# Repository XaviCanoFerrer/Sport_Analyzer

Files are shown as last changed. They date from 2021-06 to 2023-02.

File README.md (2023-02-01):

# Sport_Analyzer

Sport Analyzer is a battery powered acquisition and visualization device for measuring sport performance and rehabilitation. The device interfaces with an incremental encoder and a load cell enabling sport scientists and coaches and rehabilitators to collect and visualize the data without the need of a computer or software interaction.

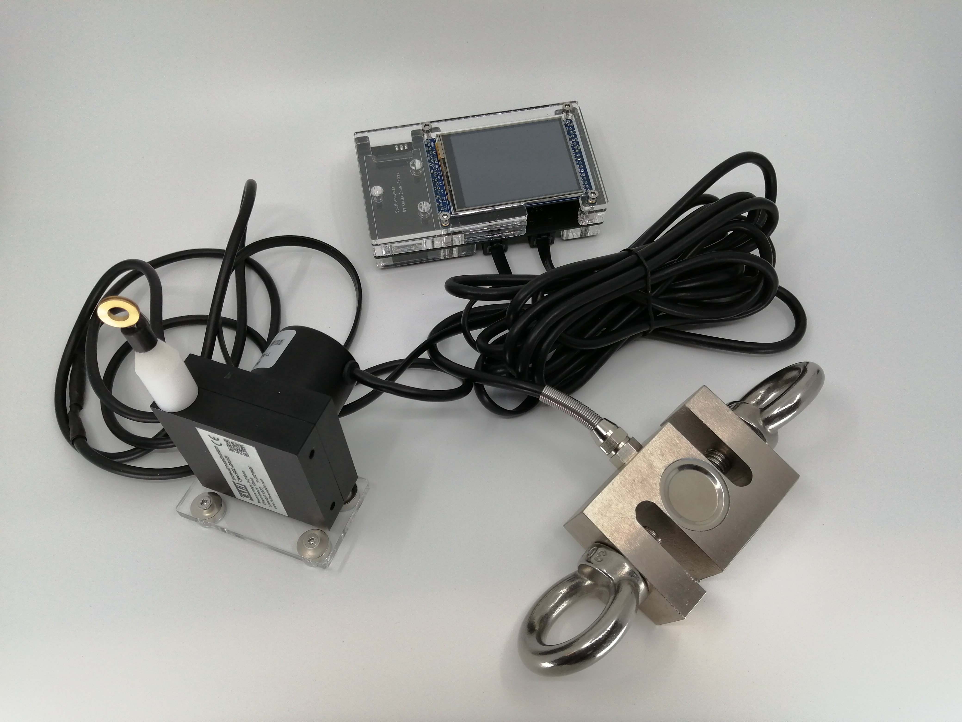
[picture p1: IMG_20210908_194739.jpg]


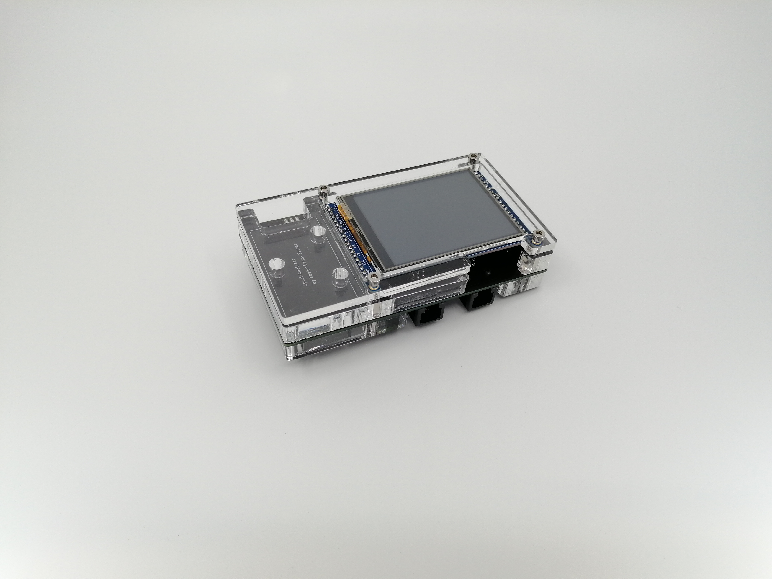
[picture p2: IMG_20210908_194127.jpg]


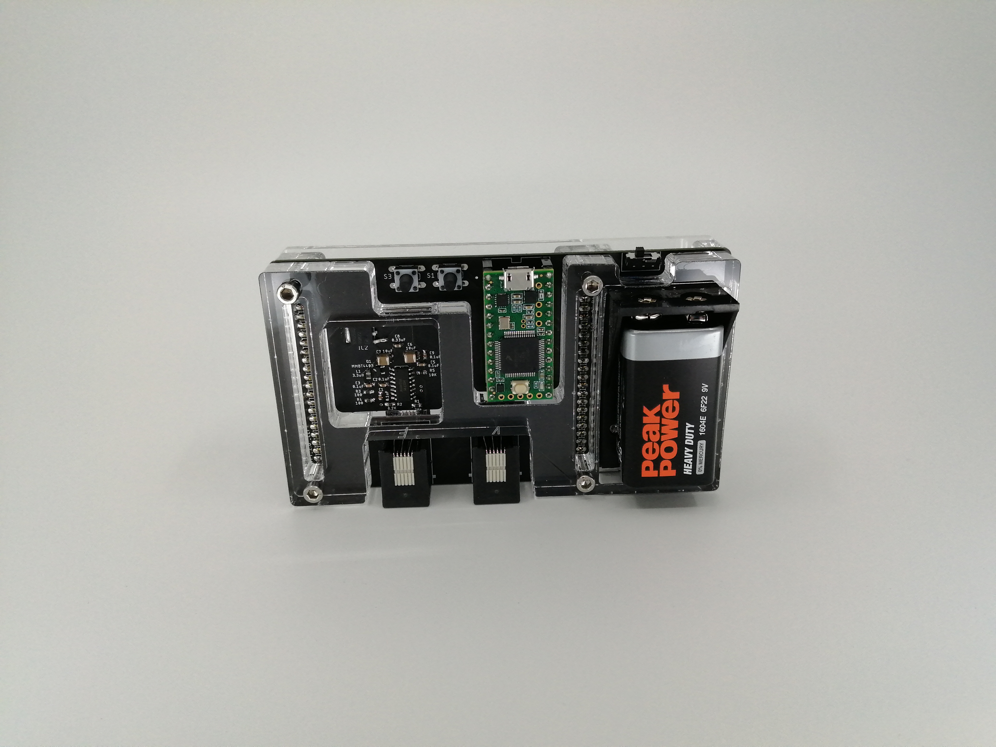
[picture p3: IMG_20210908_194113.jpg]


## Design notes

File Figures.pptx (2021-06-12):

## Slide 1

RJ12 cable – load cell connection

Cut the blue wire

E+

E-

A-

A+

Shield

Load cell wires

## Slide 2

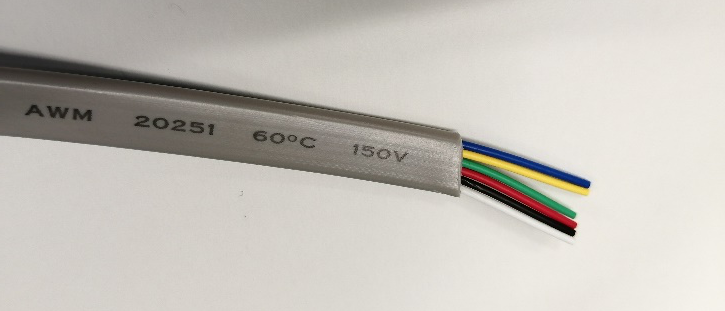
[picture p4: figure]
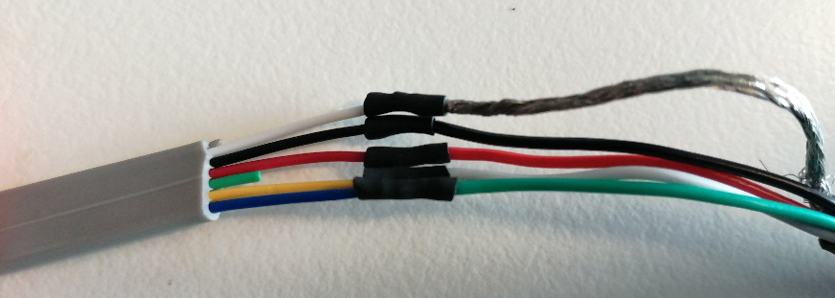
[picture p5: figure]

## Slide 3

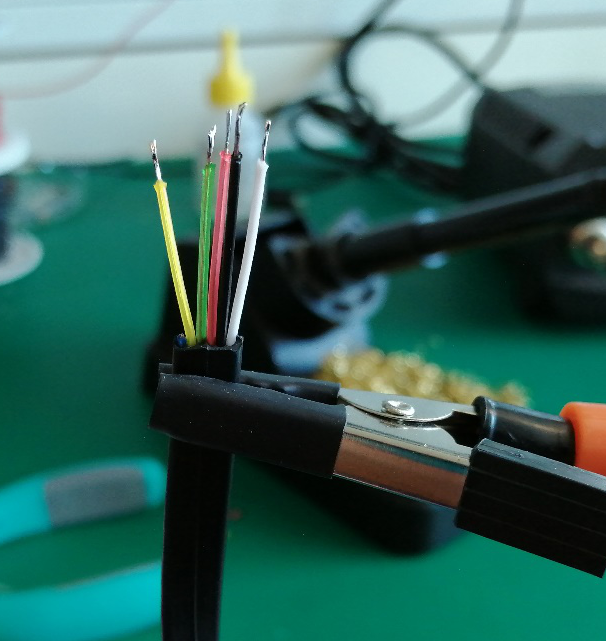
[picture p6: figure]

1

2

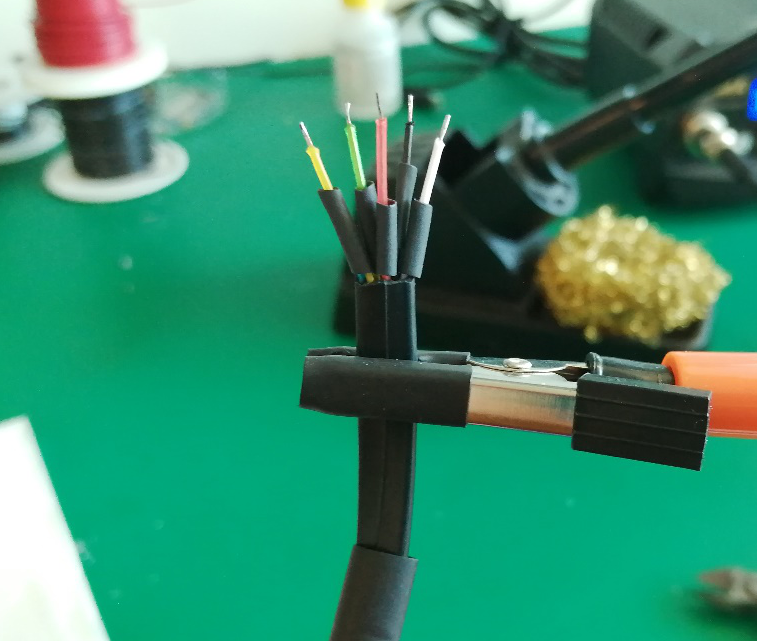
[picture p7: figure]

3

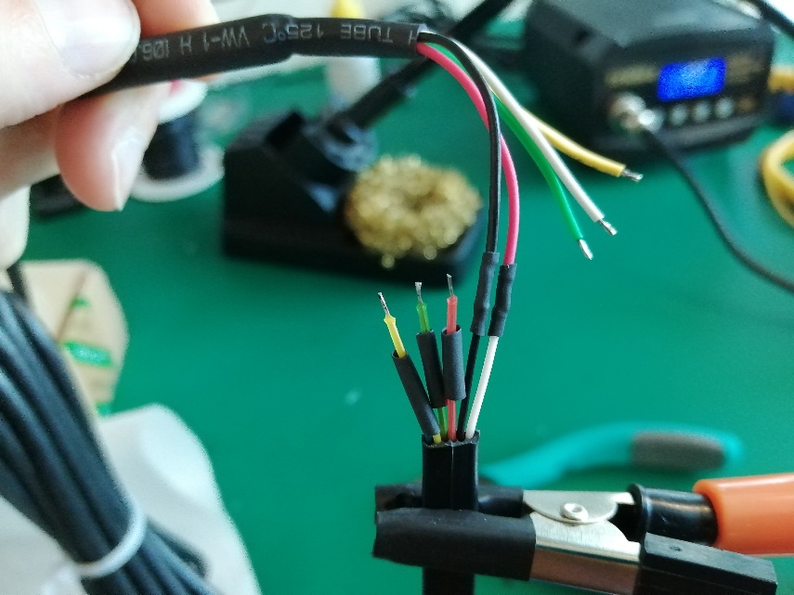
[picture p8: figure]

4

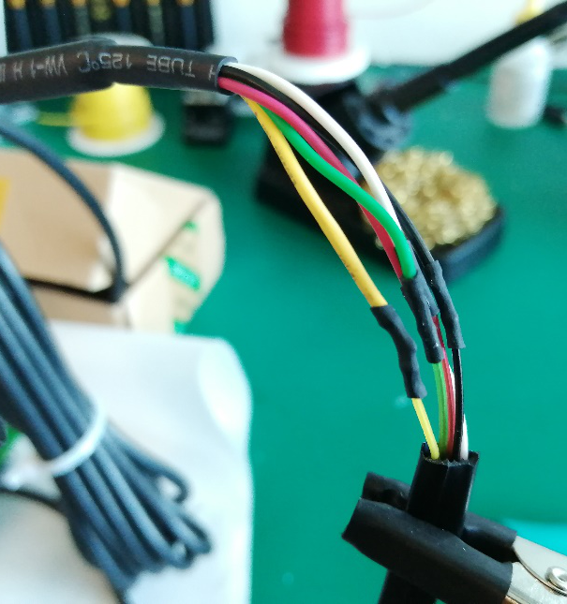
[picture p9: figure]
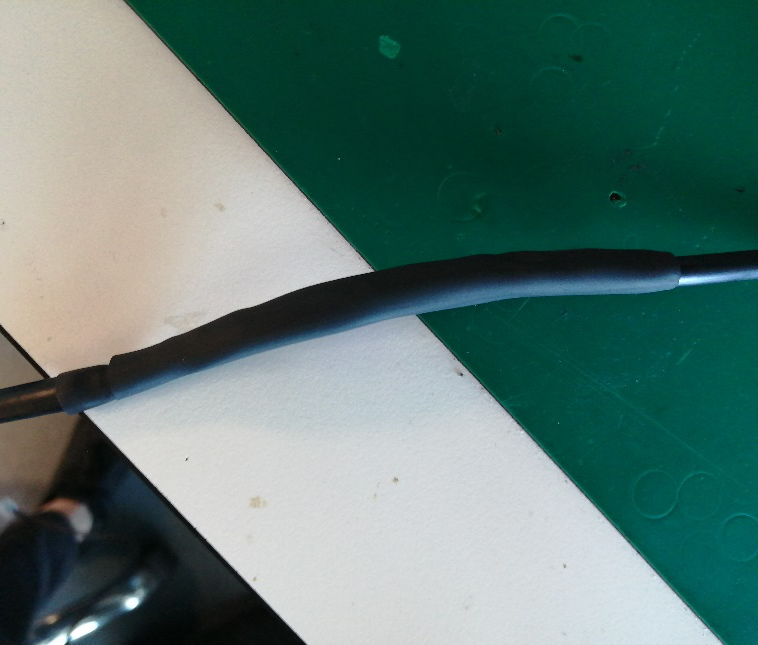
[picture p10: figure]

5

6

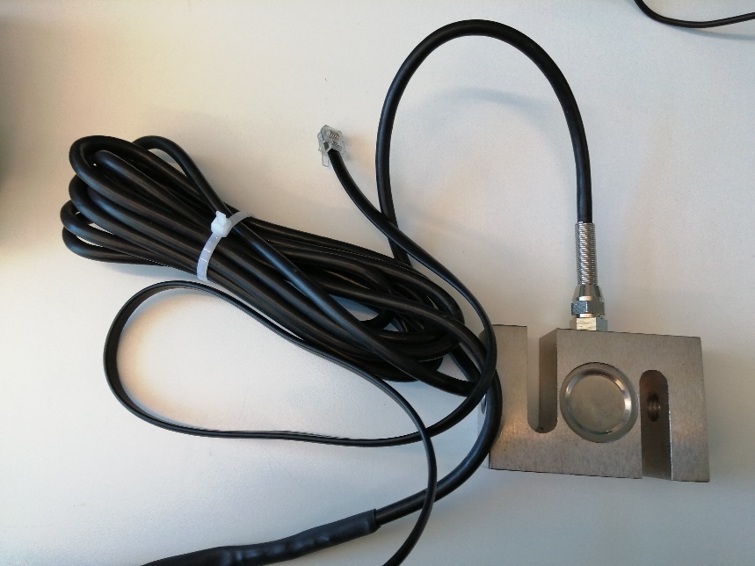
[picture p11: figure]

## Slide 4

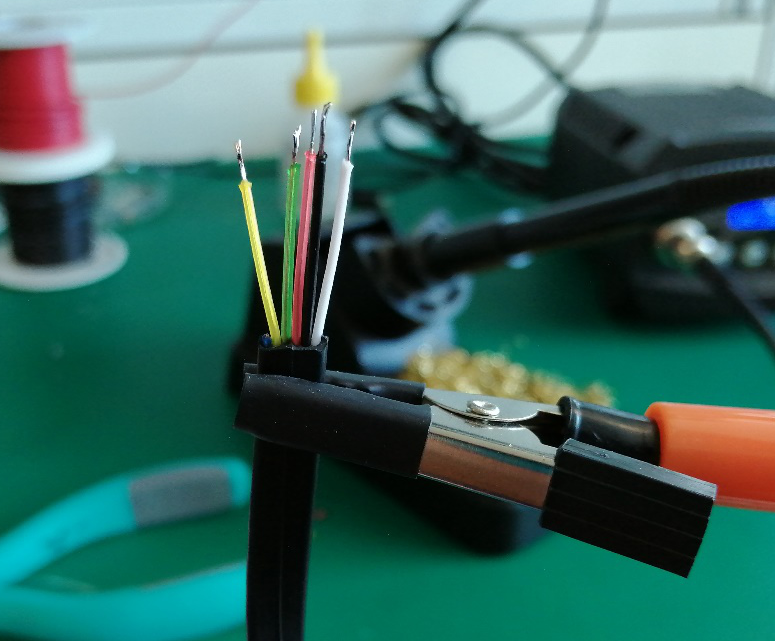
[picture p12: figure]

1

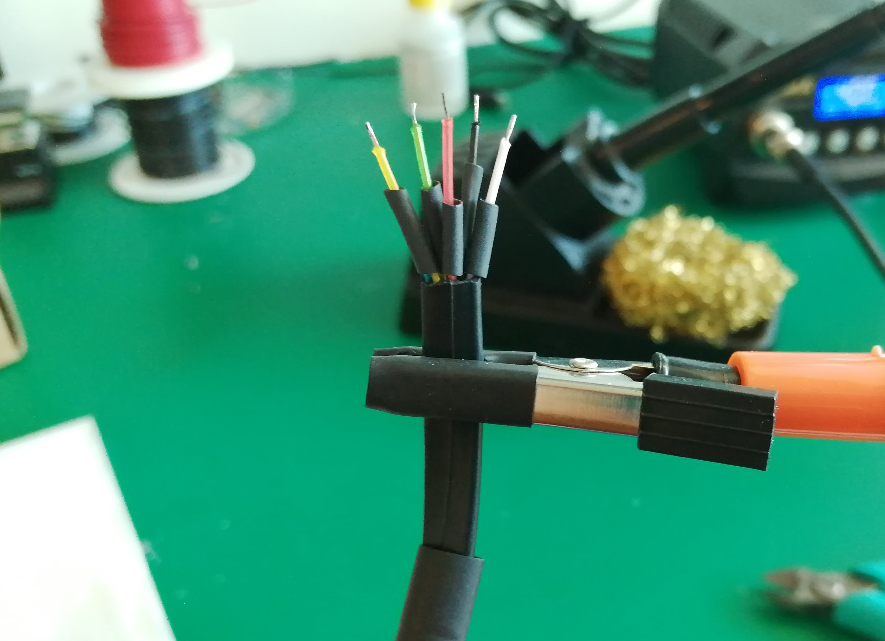
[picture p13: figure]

2

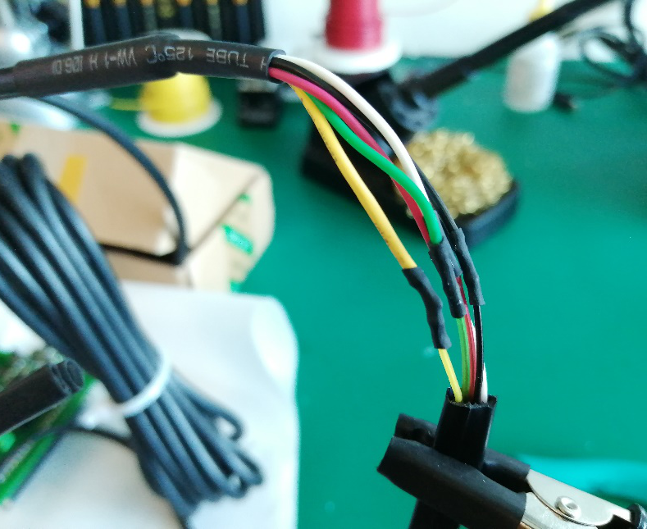
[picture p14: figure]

3

4

5

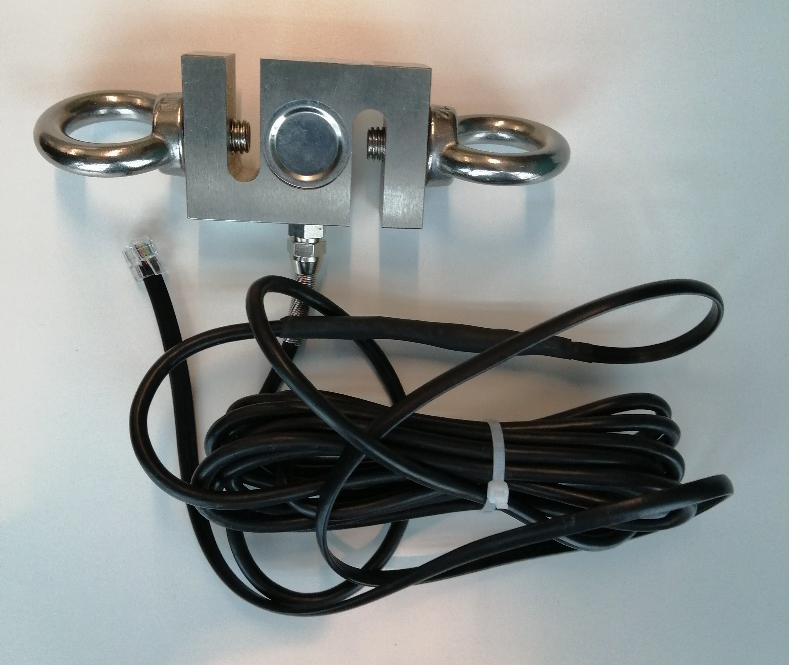
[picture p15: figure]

6

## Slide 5

RJ12 cable – optical encoder connection

Cut the green wire

Shield

GND

5V

B

A

Encoder wires

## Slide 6

RJ12 cable – load cell connection

RJ12 cable – optical encoder connection

Cut the blue wire

Cut the green wire

E+

E-

A-

A+

Shield

Shield

GND

5V

B

A

Load cell wires

Encoder wires

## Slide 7

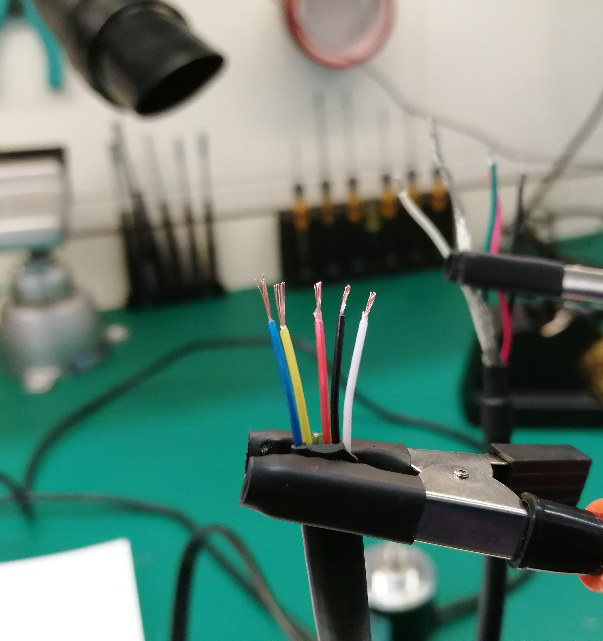
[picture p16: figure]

1

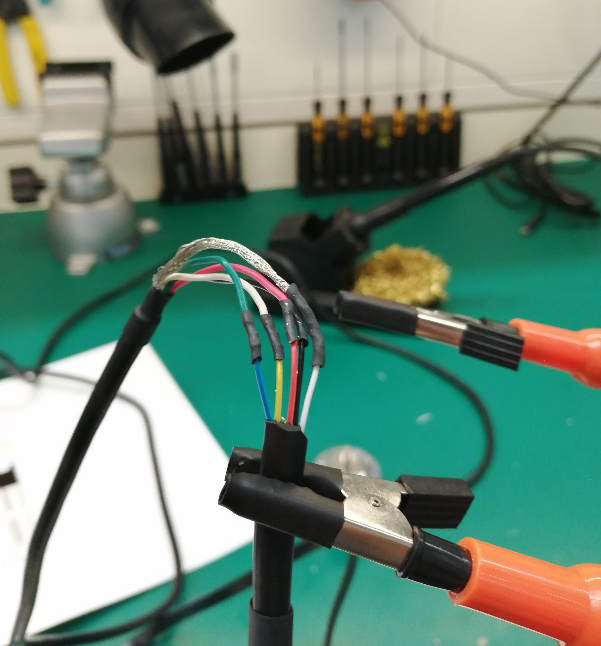
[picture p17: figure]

2

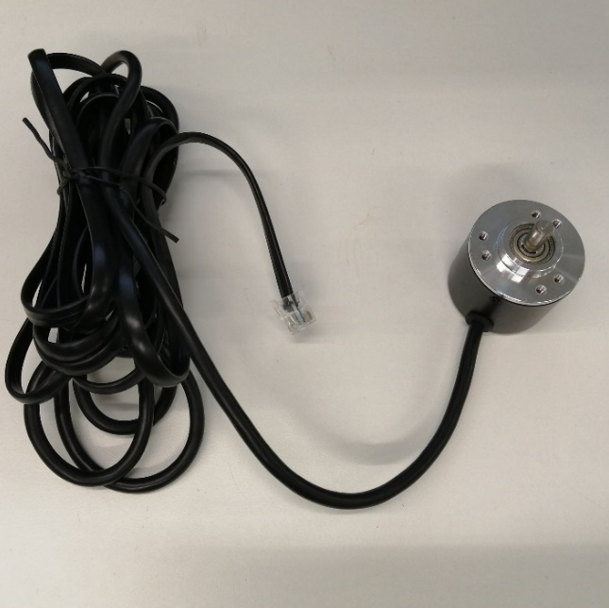
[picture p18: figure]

3

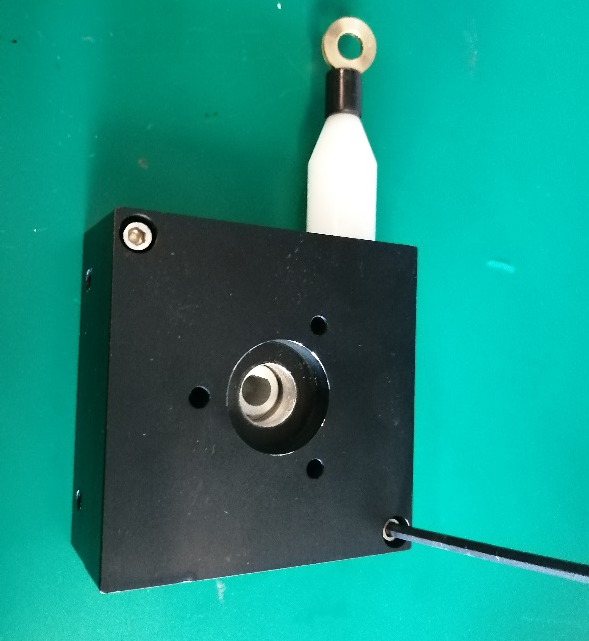
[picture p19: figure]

4

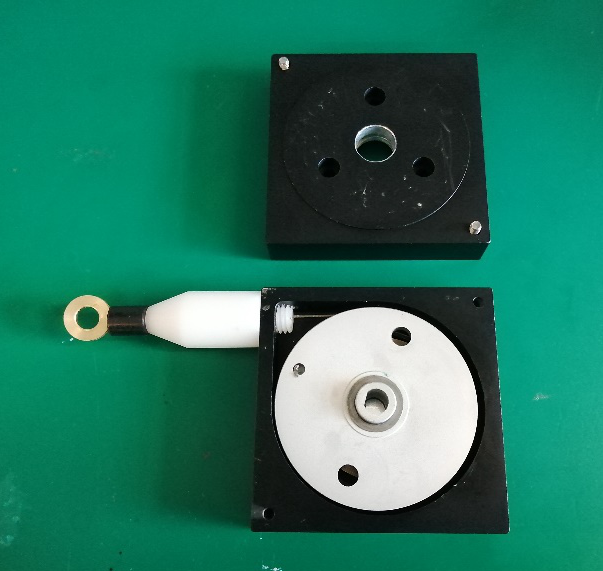
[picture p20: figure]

5

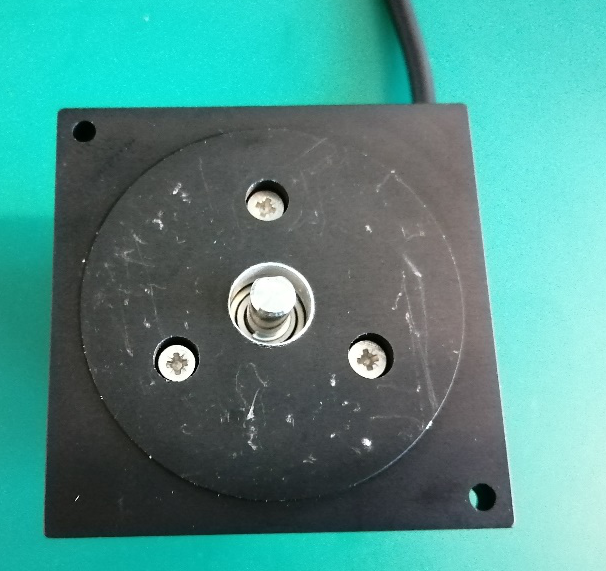
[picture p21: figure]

6

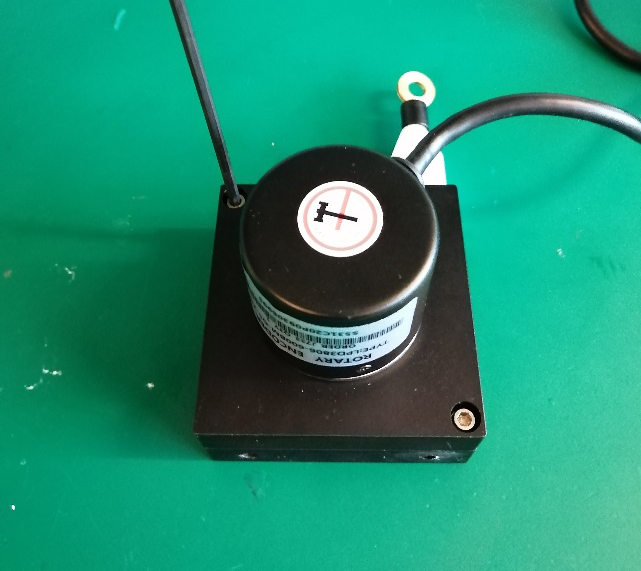
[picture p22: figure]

7

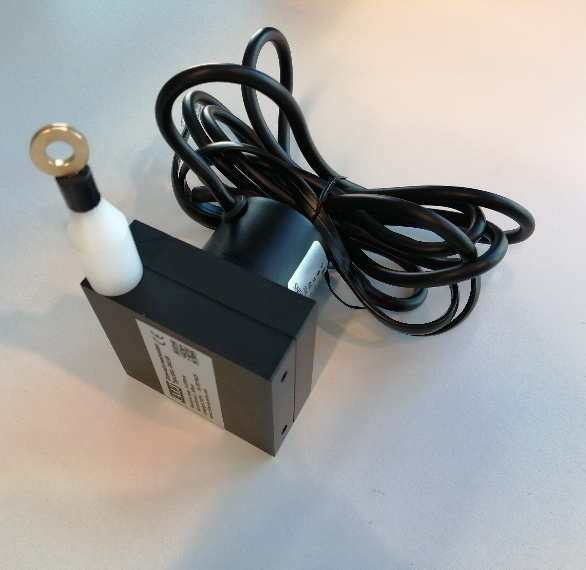
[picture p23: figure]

8

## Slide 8

RJ12 cable – resistive sensor connection

Cut the blue, yellow and white wires

5V

GND

Signal

Resistive sensor wires

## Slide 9

RJ12 cable – load cell connection

RJ12 cable – optical encoder connection

RJ12 cable – electrogoniometer connection

Cut the blue wire

Cut the green wire

Cut the blue, yellow and white wires

Load cell wires

E+

E-

A-

A+

Shield

Encoder wires

Shield

GND

5V

B

A

Electrogoniometer
sensor wires

GND

5V

Signal

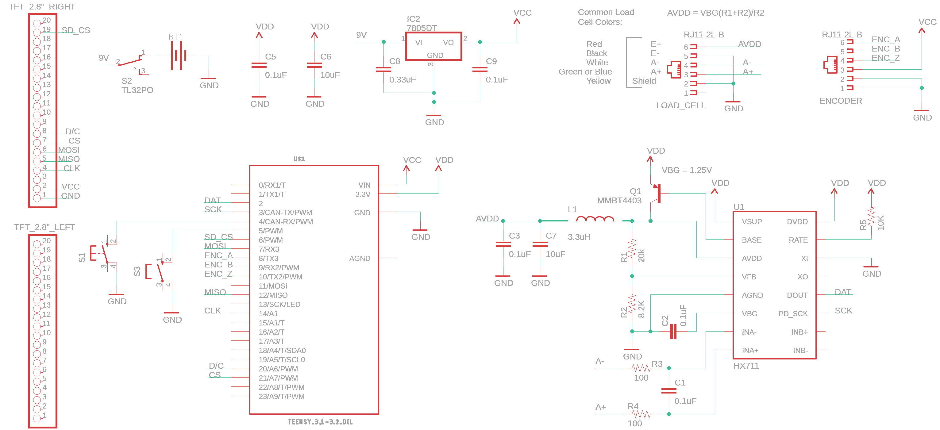
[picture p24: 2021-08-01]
Schematic.png

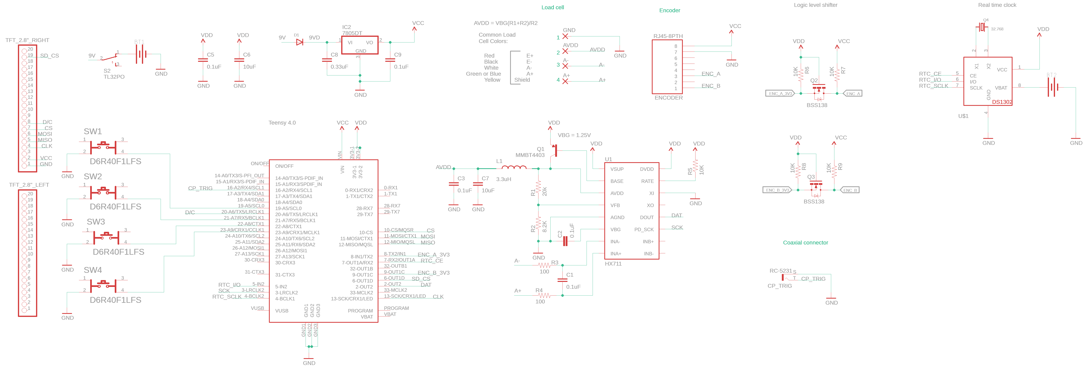
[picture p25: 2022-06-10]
Chronojump version/Teensy 4.0 version/Design files/Sport Analyzer Chronojump Teensy 4 schematic.png

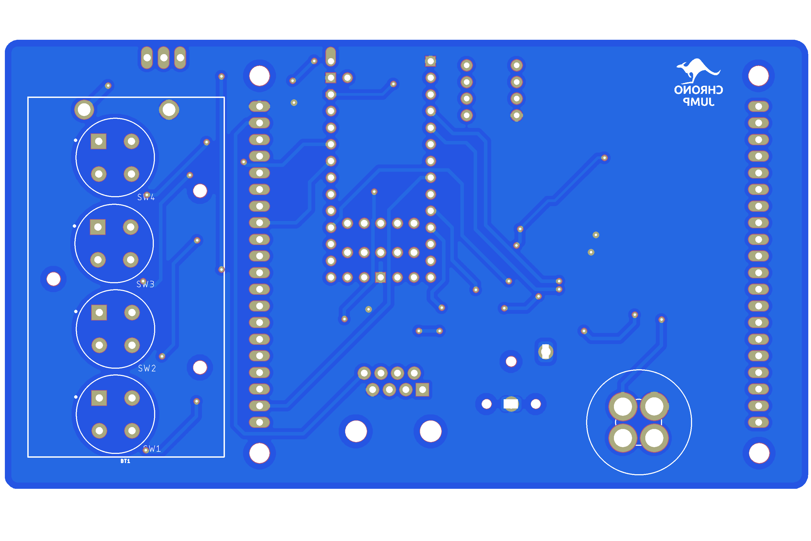
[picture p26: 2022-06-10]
Chronojump version/Teensy 4.0 version/Design files/Sport Analyzer Chronojump Teensy 4 (4 buttons)bottom.png

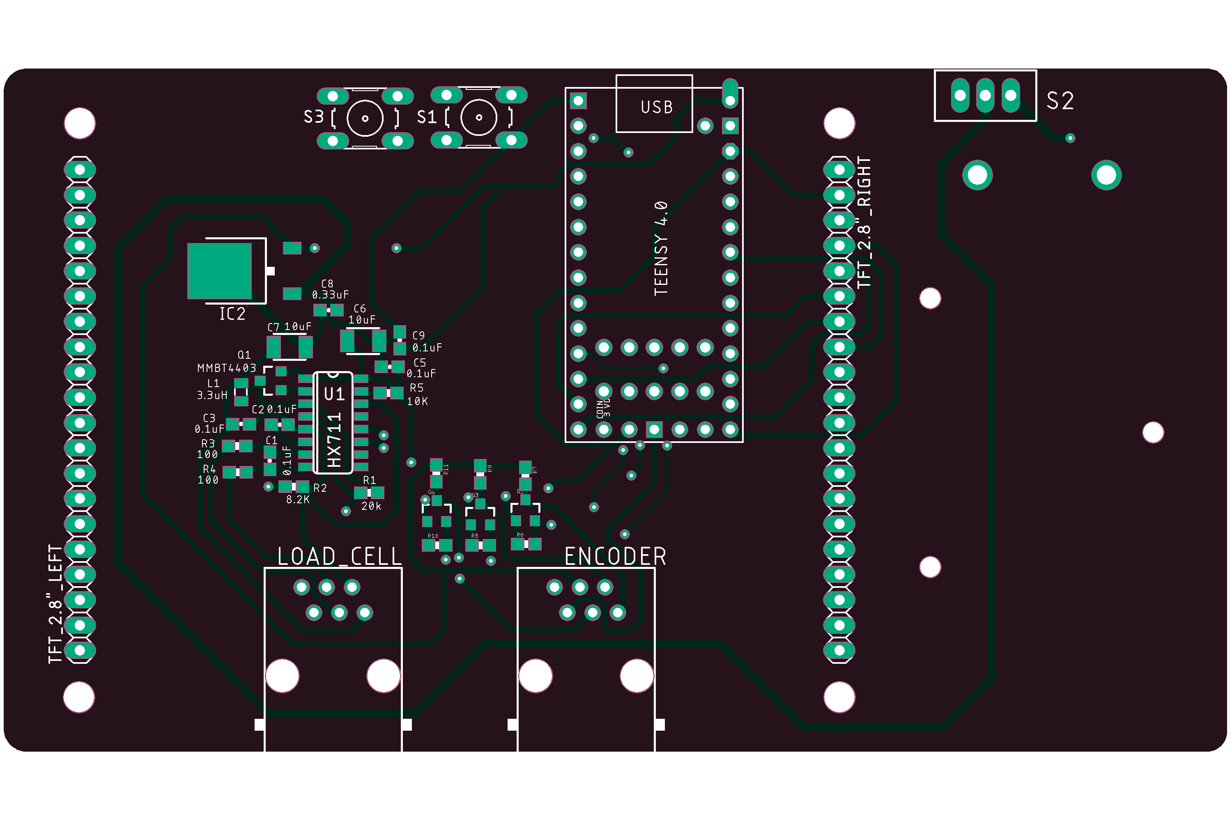
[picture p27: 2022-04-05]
Teensy 4 version/Design files/Electronics/Sport Analyzer Teensy4.png

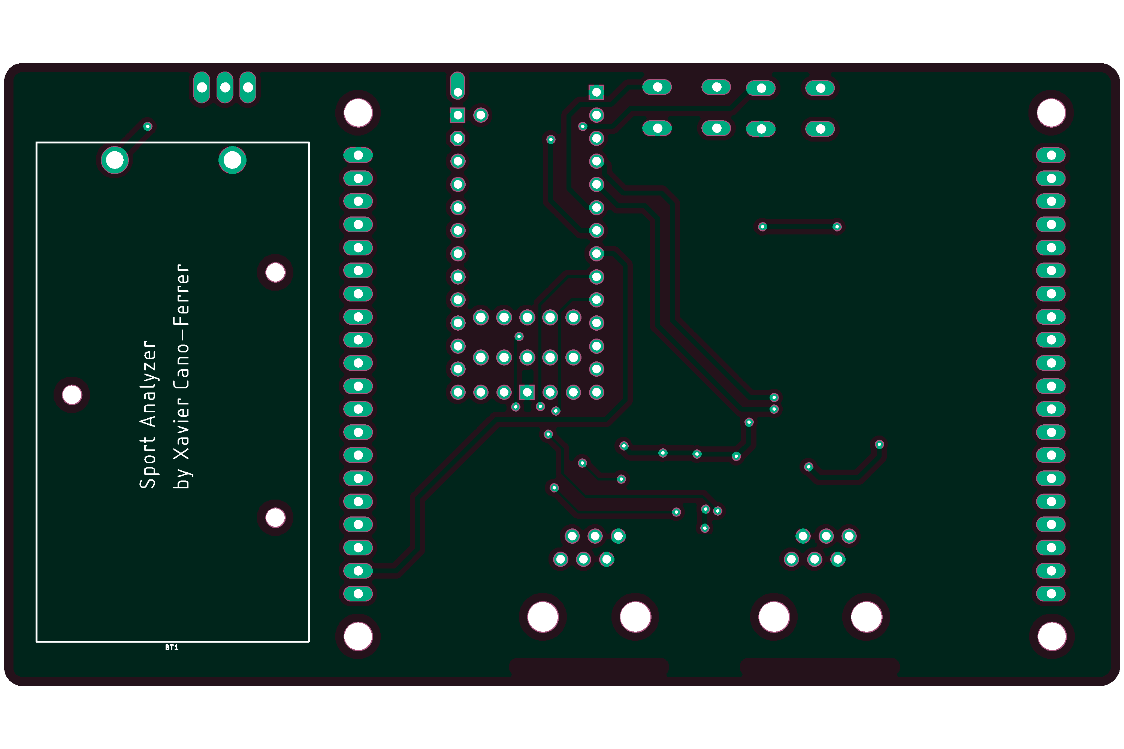
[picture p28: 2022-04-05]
Teensy 4 version/Design files/Electronics/Sport Analyzer Teensy4 bottom.png

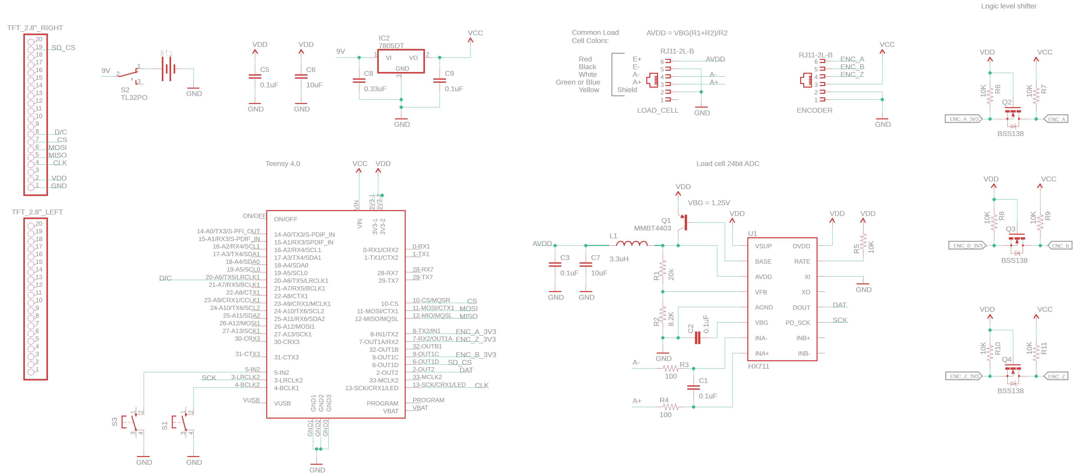
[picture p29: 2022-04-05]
Teensy 4 version/Design files/Electronics/Sport Analyzer Teensy4 schematic.png

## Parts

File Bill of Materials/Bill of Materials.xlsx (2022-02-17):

Component | Supplier | Reference | Cost per unit(£) | Quantity | Total cost
PCB | JLC PCB | - | 0.355 | 1 | 0.355
Case top | - | https://github.com/XaviCanoFerrer/Sport_Analyzer/tree/main/Manufacturing%20files |  | 1
Case middle 1 | - |  |  | 1
Case middle 2 | - |  |  | 1
Case bottom | - |  |  | 1
Encoder Base | - |  |  | 1
2.8" TFT LCD with Touchscreen Breakout Board | RS Components | 124-5469 | 27.41 | 1 | 27.41
Teensy 3.2 | CPC-Farnell | SC13983 | 16.67 | 1 | 16.67
Slide Switch | Rapid Electronics | 78-3760 | 0.374 | 1 | 0.374
RJ12 Connector | RS Components | 809-4902 | 1.36 | 2 | 2.72
Pushbutton Omron B3F-1020 | RS Components | 682-1131 | 0.586 | 2 | 1.172
Ceramic capacitor 0603 0.1uF | RS Components | 264-4646 | 0.017 | 5 | 0.085
Ceramic capacitor 0603 0.33uF | RS Components | 839-2900 | 0.142 | 1 | 0.142
Resistor 0603 100 Ω 1% | RS Components | 901-3525 | 0.05 | 2 | 0.1
Resistor 0603 10 kΩ 1% | RS Components | 901-3601 | 0.046 | 1 | 0.046
Ceramic capacitor 1210 10uF | RS Components | 766-1217 | 0.55 | 2 | 1.1
Resistor 0603 20 kΩ 1% | RS Components | 901-3610 | 0.05 | 1 | 0.05
Inductor 0805 3.3 uH | RS Components | 724-2790 | 0.164 | 1 | 0.164
Resistor 0603 8.2 kΩ 1% | RS Components | 901-3591 | 0.052 | 1 | 0.052
Transistor BJT MMBT4403 | RS Components | 739-0509 | 0.067 | 1 | 0.067
Voltage regulator 7805 | RS Components | 808-4116 | 0.5 | 1 | 0.5
HX711 Load cell ADC | JLCPCB | C43656 | 0.3522 | 1 | 0.3522
RJ12 cable | Farnell | 2070346 | 1.92 | 2 | 3.84
Female pin headers | Amazon | https://www.amazon.co.uk/Aussel-Pieces-Breakaway-Connector-Arduino-PIN-2-20PCS/dp/B01M69EA9O | 0.3495 | 3 | 1.0485
Incremental encoder | Amazon | https://www.amazon.co.uk/Wisamic-Incremental-Encoder-Dc5-24v-Voltage/dp/B015GYY7XU | 16.99 | 1 | 16.99
CALT BSL-GA55 Draw-Wire Mechanism | CALT | https://www.china-encoder.com/product/economic-version-bsl-ga55-encoder-draw-wire-mechanism/ | 32.5 | 1 | 32.5
 | CALT | https://www.aliexpress.com/item/1005002782719866.html
Loac cell | Amazon | https://www.amazon.co.uk/gp/product/B07X8PZ2HX/ref=ppx_yo_dt_b_asin_title_o02_s00?ie=UTF8&psc=1 | 29.09 | 1 | 29.09
M12 Eye bolt | Amazon | https://www.amazon.co.uk/sourcing-map-Lifting-Hanging-Stainless/dp/B08NJ32ZYY | 5.545 | 2 | 11.09
Micro SD Card 32 GB | RS Components | 123-1040 | 7.294 | 1 | 7.294
Male USB A to Male USB Micro B USB Cable, 0.5m, USB 2.0 | RS Components | 182-8551 | 3 | 1 | 3
Magnet | RS Components | 136-5467 | 7.33 | 2 | 14.66
M3 hexagonal spacers and screws | Amazon | https://www.amazon.co.uk/ANTHYTA-Standoff-Assorted-Assortment-Threaded/dp/B091KJNZLB?qsid=257-8279358-2489441 | 8.99 | 1 | 8.99
9V Battery holder | Rapid Electronics | 18-2990 | 0.48 | 1 | 0.48
 |  |  |  | Total | 179.9867

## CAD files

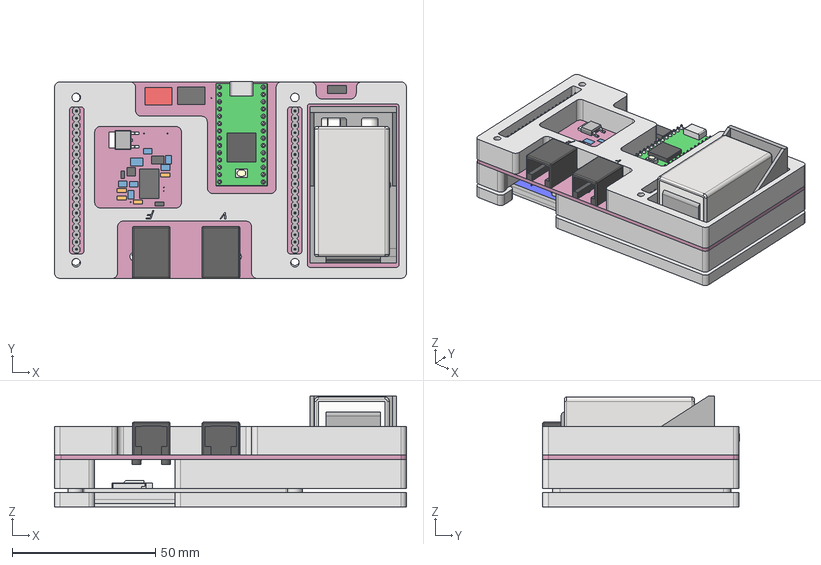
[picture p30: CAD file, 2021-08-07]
Design Files/Mechanical/Assembly.stp
122.7 x 68.7 x 38.7 mm
Bottom PMMA
Middle PMMA
Top PMMA
Adafruit 2.8TFT
RJ12 Connector x 2
9V Battery
Body_Housing
Teensy3.2
Sport Analyzer 1.0.1 PCB (2)

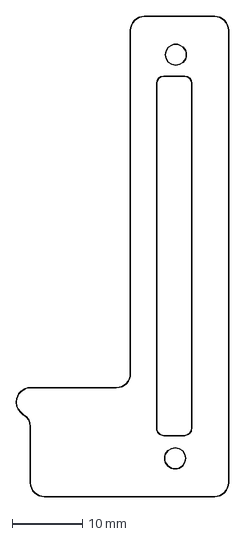
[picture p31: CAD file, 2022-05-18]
Chronojump version/Teensy 3.2 version/Manufacturing files/Case/Bottom case Chronojump 2.dxf
30.3 x 68.6 mm

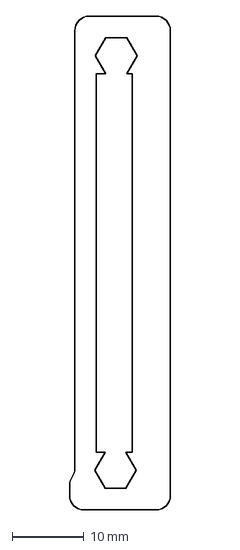
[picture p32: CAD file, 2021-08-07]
Manufacturing files/DXF files/Case Middle 2.dxf
14.0 x 68.6 mm

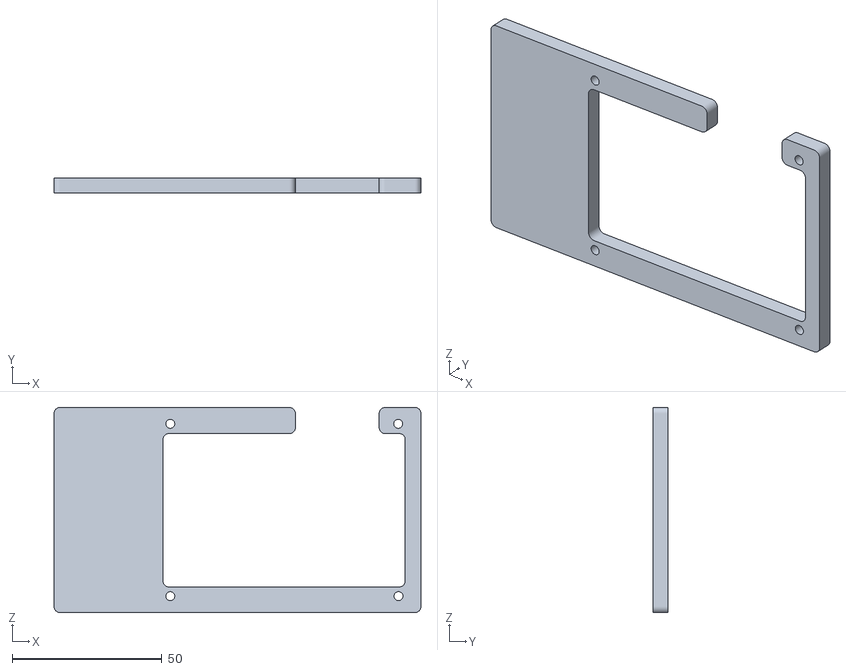
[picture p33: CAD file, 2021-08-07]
Manufacturing files/STL files/Case Top.stl
122.7 x 5.00 x 68.6

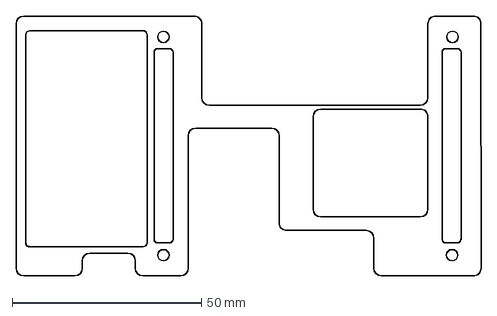
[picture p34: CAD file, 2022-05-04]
Chronojump version/Teensy 3.2 version/Manufacturing files/Case/Bottom case Chronojump 1.dxf
122.7 x 68.6 mm

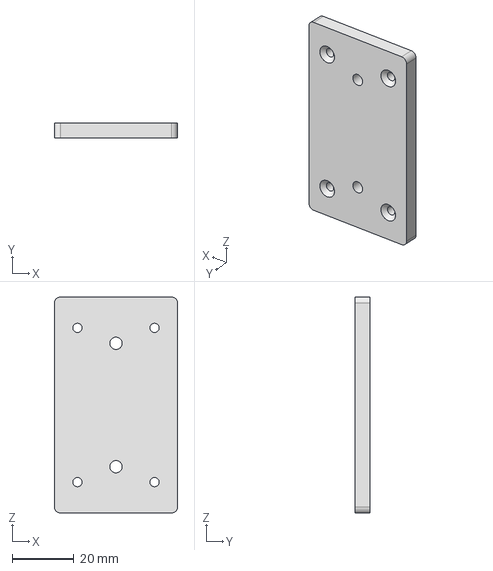
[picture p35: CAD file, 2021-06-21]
Design Files/Mechanical/Encoder base.stp
40.0 x 5.00 x 70.0 mm

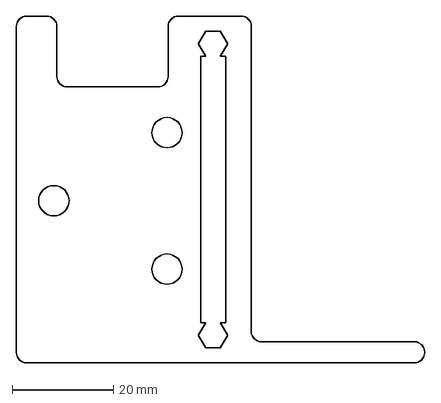
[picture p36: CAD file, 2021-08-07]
Manufacturing files/DXF files/Case Middle 1.dxf
80.7 x 68.6 mm

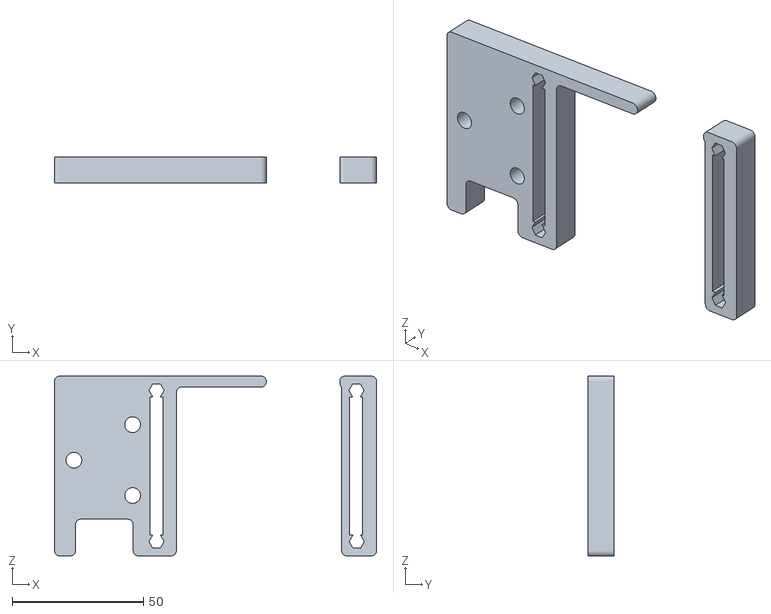
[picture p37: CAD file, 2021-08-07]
Manufacturing files/STL files/Case Middle.stl
122.7 x 10.0 x 68.6

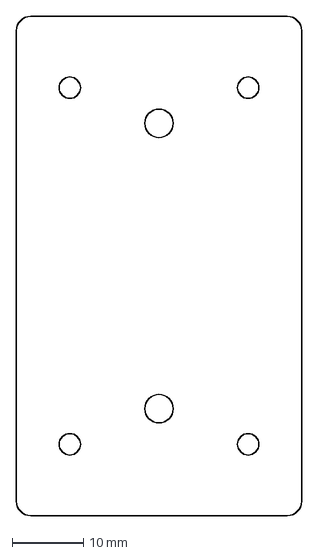
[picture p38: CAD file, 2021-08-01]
Manufacturing files/DXF files/Encoder base.dxf
40.0 x 70.0 mm

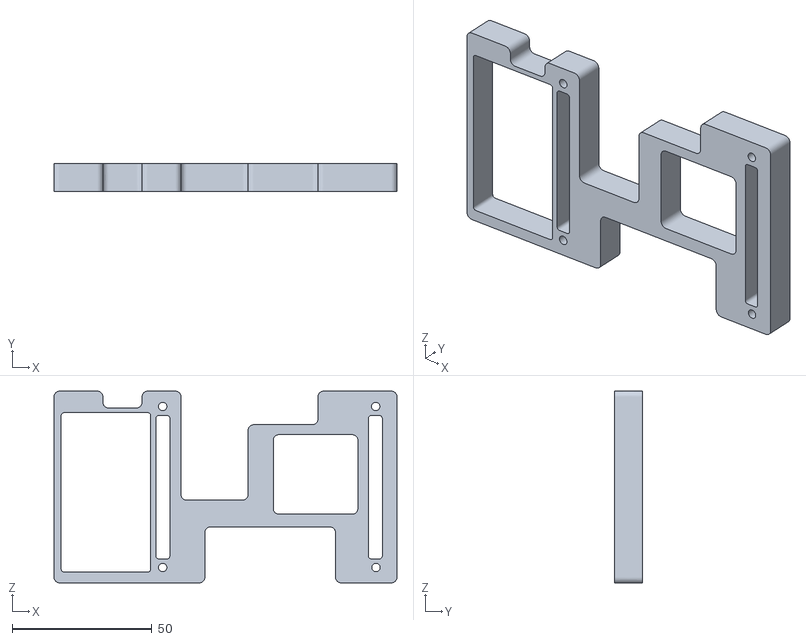
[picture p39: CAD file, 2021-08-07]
Manufacturing files/STL files/Case Bottom.stl
122.7 x 10.0 x 68.6

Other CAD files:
Chronojump version/Teensy 3.2 version/Design files/Case/Bottom PMMA Chronojump.ipt
Chronojump version/Teensy 3.2 version/Design files/Case/OldVersions/Bottom PMMA Chronojump.0021.ipt
Chronojump version/Teensy 3.2 version/Design files/Case/OldVersions/Bottom PMMA Teensy4.0018.ipt
Design Files/Mechanical/0603-CAP.ipt
Design Files/Mechanical/0603-RES.ipt
Design Files/Mechanical/0805.ipt
Design Files/Mechanical/1210.ipt
Design Files/Mechanical/1X20.ipt
Design Files/Mechanical/9V Battery.ipt
Design Files/Mechanical/Adafruit 2.8TFT.ipt
Design Files/Mechanical/Assembly3.iam
Design Files/Mechanical/B3F-10XX.ipt
Design Files/Mechanical/BATTCON_9V.ipt
Design Files/Mechanical/Board.ipt
Design Files/Mechanical/Body_Housing 9V Battery.ipt
Design Files/Mechanical/Bottom PMMA.ipt
Design Files/Mechanical/Encoder base.ipt
Design Files/Mechanical/Middle PMMA.ipt
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

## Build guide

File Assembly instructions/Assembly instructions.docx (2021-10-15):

Assembly and calibration instructions

1- Acquire the components

Order the printed circuit board and order the components described on the bill of materials: https://github.com/XaviCanoFerrer/Sport_Analyzer/tree/main/Bill%20of%20Materials. The PCB can be ordered on JLCPCB: https://jlcpcb.com/.

2- Manufacture the Sport Analyzer case

The case has been designed in a way that the components can be laser cut or 3D printed, which are the two most common manufacturing processes available for makers (Figure 1). The files can be found on https://github.com/XaviCanoFerrer/Sport_Analyzer/tree/main/Manufacturing%20files.

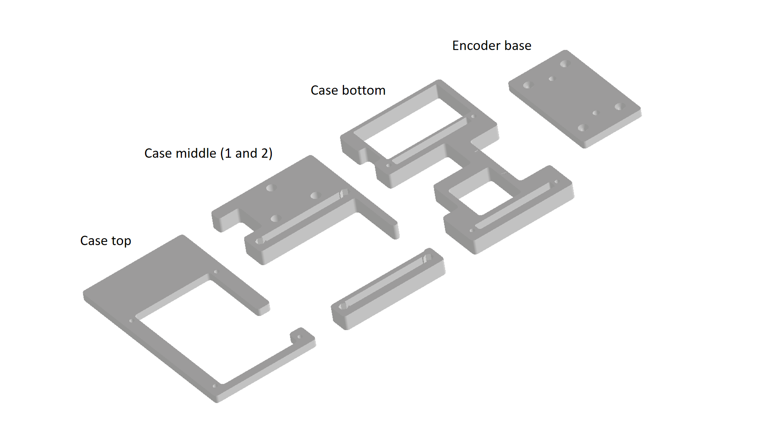
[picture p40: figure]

Figure 1: Components of the case.

3- Solder the components on the Board

In order to hold the surface mount components (SMD) it is highly recommended to use tweezers to hold the small capacitors and resistors. All components can be soldered by adding solder on one of the pads and then fuse the solder by touching it with the soldering iron while holding the component in place helping yourself with the tweezers (Figure 2).

Figure 2: Components to be soldered.

4- Case assembly

The three components of the case (top, middle and bottom) are assembled using four hexagonal spacers and eight M3 screws that hold them together (Figure 3).

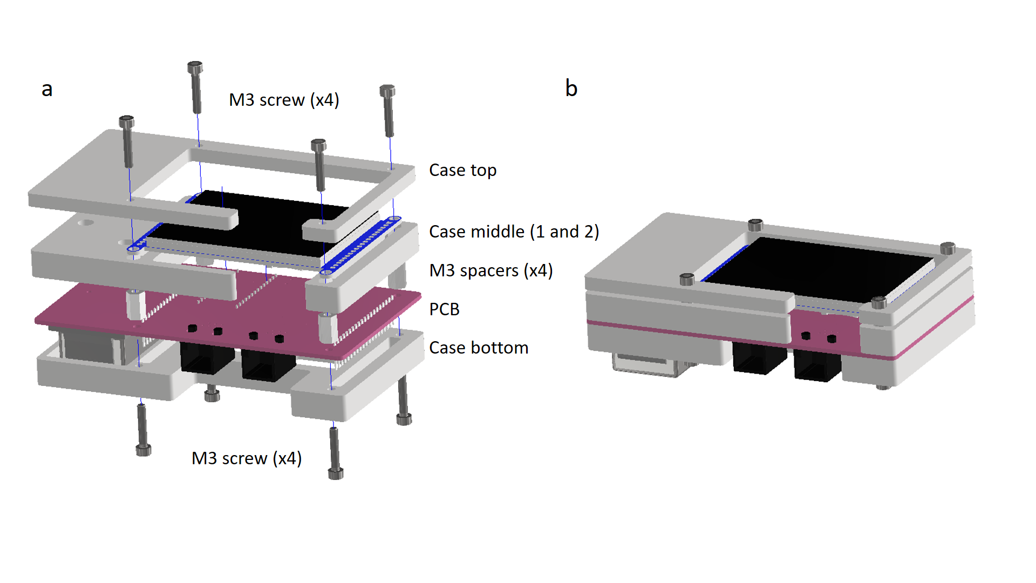
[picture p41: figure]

Figure 3: Exploded and assembled views of the case with the board.

5- RJ12 cable connections

The load cell and the encoder are connected with the Sport Analyzer using RJ12 (6 wire) connections. In Figure 4 is described which wires must be soldered with which ones to have a successful connection with the sensor leads.

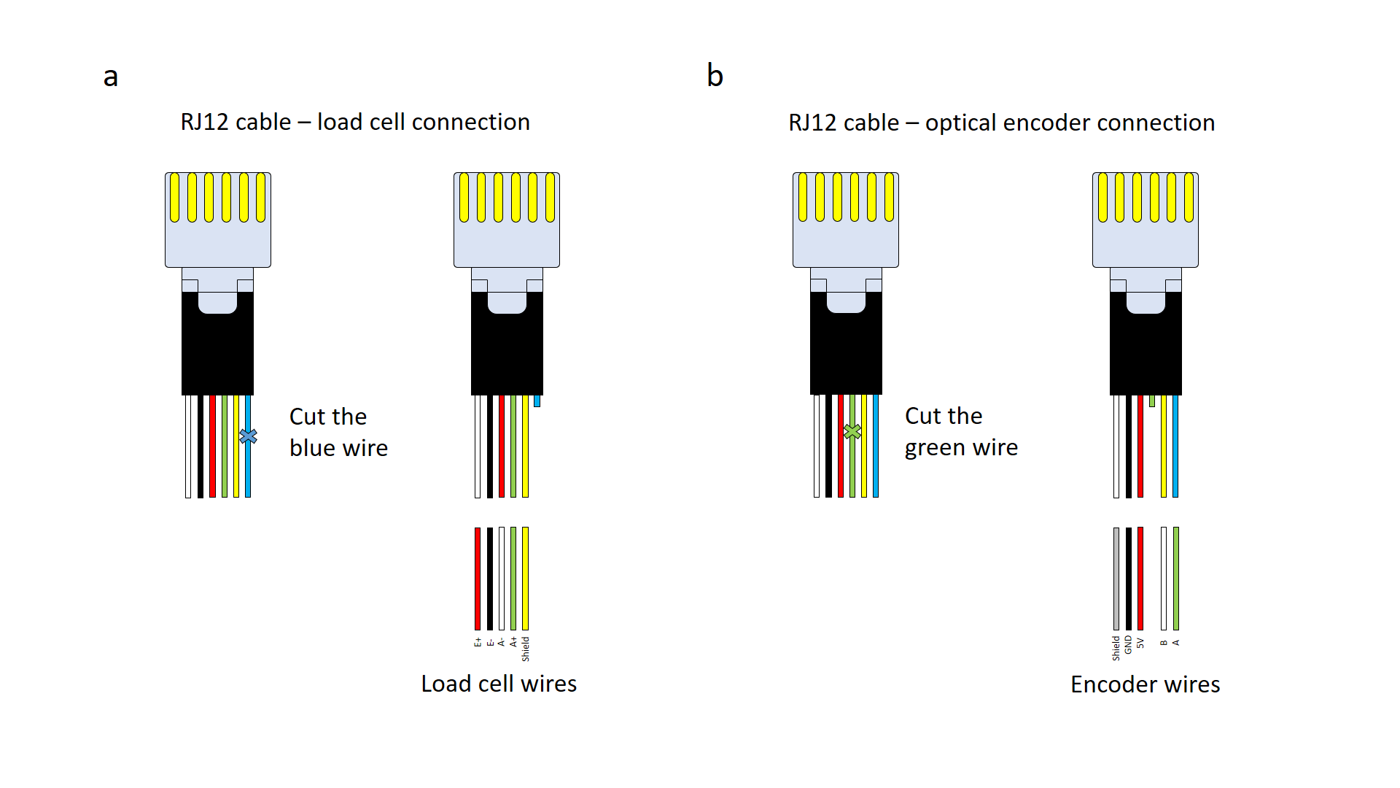
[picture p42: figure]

Figure 4: RJ12 cable connections for the load cell and the encoder.

6- Load cell building

The only manufacturing process on the load cell side is the soldering of the RJ12 cable with the load cell cable as described on (Figure 4a). The RJ12 cable must be strip leaving approximately 30 cm of cable from the connector to the cut. Then solder can be applied on each of the wires of both sides (Figure 5a). A big heat shrink with bigger diameter than the cable and six smaller ones can be applied on the wires (Figure 5b). Then solder each of the wires one by one and apply heat on the small heat shrinks (Figure 5c). Now surround the five small wires with the big heat shrink and apply heat getting a continuous cable again (Figure 5d-e). The final step is to screw the M12 eye bolts on both sides of the load cell (Figure 5f).

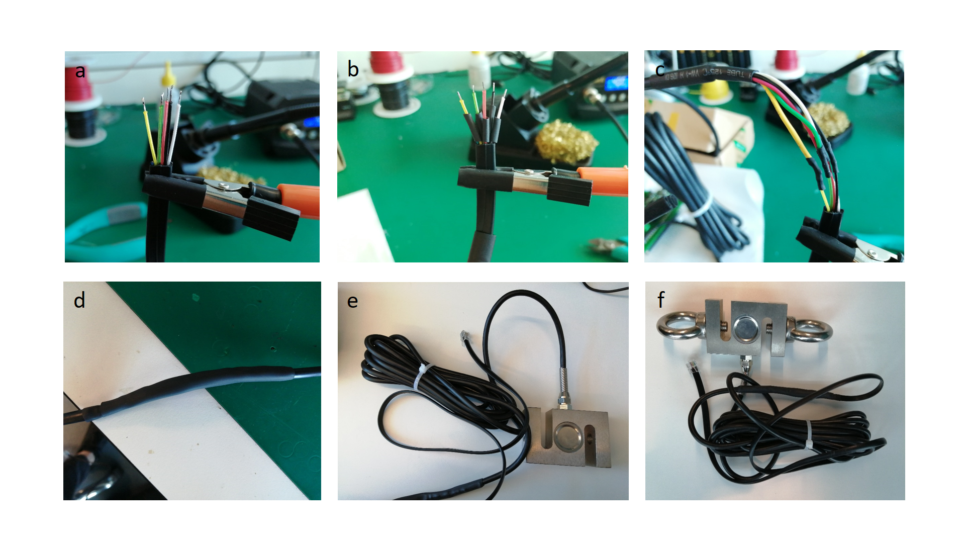
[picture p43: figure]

Figure 5. Load cell soldering and assembly process.

7- Encoder building

The encoder soldering process is very similar to the one described with the load cell. How to connect the sensor cables with the RJ12 connector can be found in Figure 4b. The RJ12 cable must be strip leaving approximately 30 cm of cable from the connector to the cut. Then solder can be applied on each of the wires of both sides (Figure 6a). A big heat shrink with bigger diameter than the cable and six smaller ones can be applied on the wires. Then solder each of the wires one by one and apply heat on the small heat shrinks (Figure 6b). Now surround the five small wires with the big heat shrink and apply heat getting a continuous cable again (Figure 6c). The next steps describe how to assemble the incremental encoder with the draw-wire mechanism which converts the rotational movement into translational movement. Place the draw-wire mechanism facing the Allen key screws up. Both M3 screws have to be removed (Figure 6d). Then the top part has to be carefully lifted keeping the rotary part in the original position (Figure 6e), this is important because it is keeping the spring in place and if lifted the spring will come off being really difficult to put back. Then use 3 M3 screws to attach the incremental encoder with the top part (Figure 6f). Attach the top part with the bottom part placing the encoder shaft inside the rotary part and attaching bottom and top with the two M3 screws previously removed (Figure 6g). The linear encoder assembly is completed (Figure 6h). The same process can be found on the following link provided by the manufacturing company: https://www.youtube.com/playlist?list=PLo6Bmj-F0yyxRFb8ynPXJDACgFAKuwAJT.

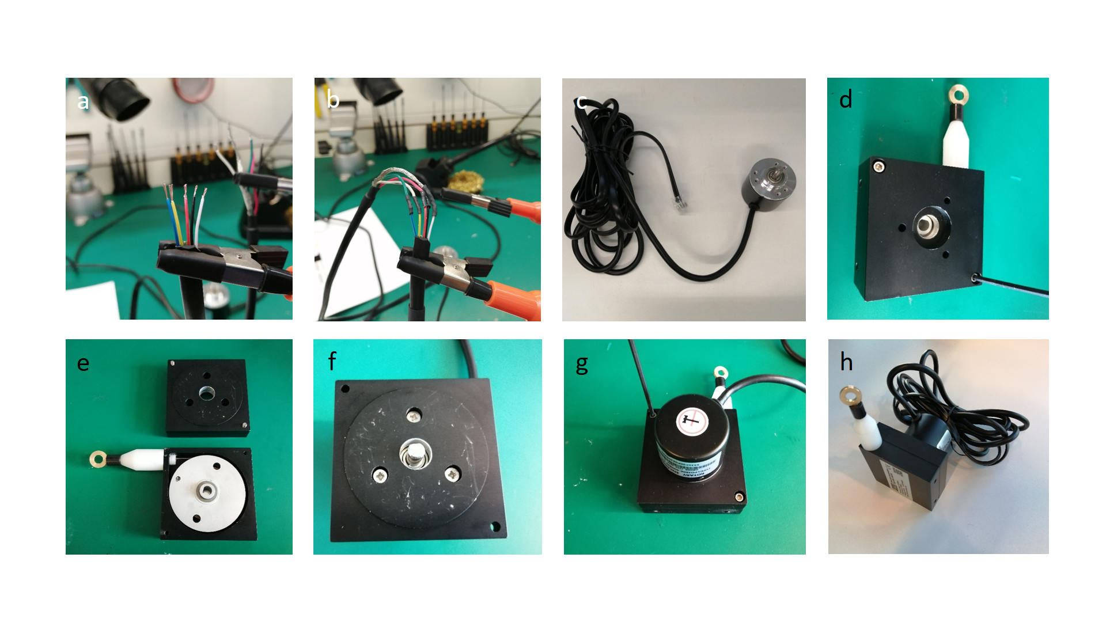
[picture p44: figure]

Figure 6. Linear encoder soldering and assembly process.

8- Encoder base building

Make chamfers on the 3 mm holes of the encoder base. Attach the magnets with the encoder base using four M3 screws. Then attach the encoder base with two M4 screws (10 mm length).

Figure 7. Base building and assembly.

9- Load cell calibration

Open the excel file: Load cell calibration.xlsx that can be found on: https://github.com/XaviCanoFerrer/Sport_Analyzer/tree/main/Calibration/Load%20cell%20calibration. Upload the calibration program to the Sport Analyzer https://github.com/XaviCanoFerrer/Sport_Analyzer/tree/main/Calibration/Calibration. For this calibration you are going to need five different weights to get a five-point calibration equation. Weight the load cell using a scale and add the weight on the excel file on the “Load cell weight” field. Attach the load cell on one side using a rigid rope or strap. Then hang each of the weights from the load cell and introduce the weight and the sensor value you can see on the screen. Repeat this step for each of the weights. Then you will see the calibration equation displayed on the excel scatter plot. Download and open the Firmware.ino https://github.com/XaviCanoFerrer/Sport_Analyzer/tree/main/Firmware/Sport_Analayzer_1.0 and replace the load cell equation by your equation and save the file.

10- Encoder calibration

Open the excel file: Encoder calibration.xlsx that can be found on: https://github.com/XaviCanoFerrer/Sport_Analyzer/tree/main/Calibration/Encoder%20calibration. Upload the calibration program to the Sport Analyzer https://github.com/XaviCanoFerrer/Sport_Analyzer/tree/main/Calibration/Calibration. Hold a 50 cm ruler on a flat surface with tape. Perform the proposed measurements and add them one by one to the excel sheet. The excel sheet will calculate the average pulses per millimetre and it inverse millimetre per pulse. In case the encoder resolution is different from the encoder proposed replace the encoder resolution constant on the Firmware.ino program as done before with the load cell equation.

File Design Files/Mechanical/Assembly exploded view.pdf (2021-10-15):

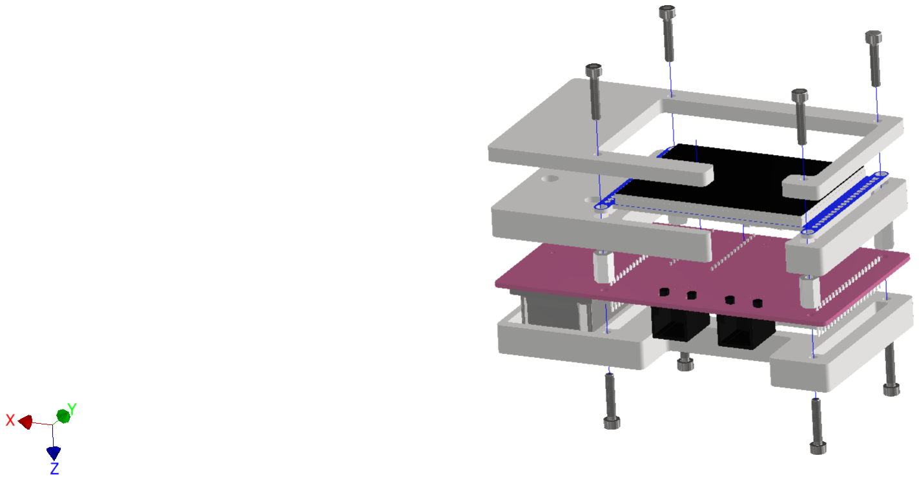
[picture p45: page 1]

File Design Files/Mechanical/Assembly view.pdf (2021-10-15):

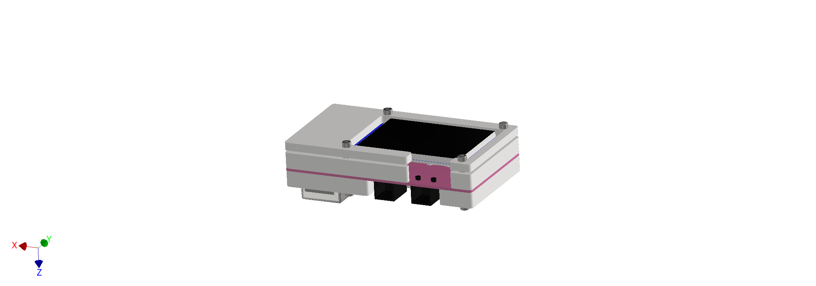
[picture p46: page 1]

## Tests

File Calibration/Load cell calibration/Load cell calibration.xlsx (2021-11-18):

Load cell mass (kg) | 0.8
Gravity | 9.81
Mass suspended(kg) | Force (N) | Sensor value
0 | 0 | 2900
8 | 86.328 | 75700
12 | 125.568 | 110900
16 | 164.808 | 145400
20 | 204.048 | 180200
24 | 243.288 | 215300
28 | 282.528 | 250200
32 | 321.768 | 284800

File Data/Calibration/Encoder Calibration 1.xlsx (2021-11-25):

0 | 0 | 0 |  | Average 500 mm measurements |  |  |  | 7846
0 | 0 | 1 |  |  |  |  |  | 7846
0 | 0 | 2
0 | 0 | 3 |  | 7845.683374 | 7846
0 | 0 | 4 |  | 8.0899023 | pulses
0 | 0 | 5 |  | 0.1031127808 | %
0 | 0 | 6 |  | 0.001031127808
0 | 0 | 7
0 | 0 | 8 |  | pulses/mm | 15.692
0 | 0 | 9 |  | mm/pulse | 0.06372673974
0 | 0 | 10
0 | 0 | 11
0 | 0 | 12 |  | 15 | N = 15
0 | 0 | 13
0 | 0 | 14
0 | 0 | 15 |  | pulses/mm | 15.692 | ± | 0.01618045756
0 | 0 | 16 |  |  | 0.06372673974
0 | 0 | 17
0 | 0 | 18
0 | 0 | 19
0 | 0 | 20
0 | 0 | 21
0 | 0 | 22
0 | 0 | 23
0 | 0 | 24
0 | 0 | 25
0 | 0 | 26
0 | 0 | 27
0 | 0 | 28
0 | 0 | 29
0 | 0 | 30
0 | 0 | 31
0 | 0 | 32
0 | 0 | 33
0 | 0 | 34
0 | 0 | 35
0 | 0 | 36
0 | 0 | 37
0 | 0 | 38
0 | 0 | 39
0 | 0 | 40
0 | 0 | 41
0 | 0 | 42
0 | 0 | 43
0 | 0 | 44
0 | 0 | 45
0 | 0 | 46
0 | 0 | 47
0 | 0 | 48
0 | 0 | 49
0 | 0 | 50
0 | 0 | 51
0 | 0 | 52
0 | 0 | 53
0 | 0 | 54
0 | 0 | 55
0 | 0 | 56
0 | 0 | 57
0 | 0 | 58
0 | 0 | 59
0 | 0 | 60
0 | 0 | 61
0 | 0 | 62
0 | 0 | 63
0 | 0 | 64
0 | 0 | 65
0 | 0 | 66
0 | 0 | 67
0 | 0 | 68
0 | 0 | 69
0 | 0 | 70
0 | 0 | 71
0 | 0 | 72
0 | 0 | 73
0 | 0 | 74
0 | 0 | 75
0 | 0 | 76
0 | 0 | 77
0 | 0 | 78
0 | 0 | 79
0 | 0 | 80
0 | 0 | 81
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

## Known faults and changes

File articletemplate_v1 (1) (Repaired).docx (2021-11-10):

# Template of Hardware Metapaper

For submission to the Journal of Open Hardware

To complete this template, please replace the blue text with your own. The paper has five main sections: (1) Overview; (2) Quality Control; (3) Application (4) Build Details (5) Discussion.

# (1) Overview

## Title

The title of the hardware paper should focus on the hardware, e.g. “[type of hardware] to automate laboratory protocol X” or “Surface Trawl for Collecting Marine Microplastics.” If the hardware is closely linked to a specific research paper, then “[Hardware type] from [Paper Title]” is appropriate. The title should relate to the functionality of the hardware and the area it relates, to rather than making claims about the usability or user characteristics of hardware, e.g. “Easy-to-use”.

## Sport Analyzer: Multi-sensor device for data acquisition and visualization in sport performance and rehabilitation.

## Paper authors

1. Last name, first name; (Lead/corresponding author first)

2. Last name, first name; etc.

1. Cano-Ferrer Xavier (First/corresponding Author)

2. Imbert, Albane

## Paper author roles and affiliations

1. First author role and affiliation

2. Second author role and affiliation etc.

1. Research Engineer, Making Science Technology Platform, The Francis Crick Institute, London, United Kingdom

2. Head, Making Science Technology Platform, The Francis Crick Institute, London, United Kingdom

Note: One author can have multiple affiliations and affiliations can include “independent”.

## Abstract

A short (up to 250 words) summary of the hardware being described: what problem(s) the hardware addresses, what it does, how it technically/methodologically advances the state-of-the-art, how it was designed and implemented, and its applicability to other issues/research/areas of reuse.

In this paper we introduce Sport Analyzer, a battery powered device which records and displays force and velocity signals simultaneously and a small footprint. It provides a universal interface circuit for optical incremental encoders and load cells and calibration guides that will allow sport scientists, physiotherapists and medical scientists to build their own hardware and understand how to convert an industrial sensor in a human movement device.

## Metadata Overview

Please provide the following overview and self-assessment

Main design files: link to repository with design files and assembly instructions https://github.com/XaviCanoFerrer/Sport_Analyzer

Target group: e.g. secondary school students, layperson, undergraduate students, scientists in [discipline], trained engineers, use of professional services

Scientists, professionals or undergraduate students in the following disciplines: sport science, sports medicine, physiotherapy, biomechanics.

Skills required: For each main manufacturing method, provide information pairs (method - easy / advanced / specialist). E.g. desktop 3d printing - easy; surface mount PCB - advanced; injection moulding – specialist

Laser ablation – easy; Mechanical assembly – easy; Electrical assembly – advanced; Software – easy.

Replication: Project has been replicated at time of publication? Include reference (possibly way of contact). Links to places where future builds and kits might be found (repository, group website, collaboration site, etc.).

See section “Build Details” for more detail.

No builds known to the authors so far. Device has been used by authors for a paper currently in preparation.

## Keywords

(required) keyword 1; keyword 2; etc.

Keywords should make it easy to identify who and what the hardware will be useful for. Maximum of 5 keywords. E.g.: microbiology; laboratory; microfluidics; single cell analysis; fluorescence

Biomechanics, power-oriented resistance training, rehabilitation, sport science, encoder.

## Introduction

An overview of the hardware, what it does, how it was produced, and the research for which it has been used. If the hardware addresses a specific lack or problem, describe the problem in this section and how the hardware addresses the problem. Elaborate how it technically/methodologically advances the state-of-the-art including references to relevant research articles and online references.

In Sports science, sports medicine and physiotherapy two of the most valuable mechanical variables that can be used to control performance, fitness and health are force and velocity. It is well established the use of certain movements or tests to evaluate imbalances that can be related to pathologies or injuries as well as sport gesture performance analysis that can be correlated with a specific training program or method. Between all sensors used for sport performance and rehabilitation, incremental encoders and load cells are some of the most effective to measure velocities and forces associated with physical evaluation tests or exercises. In the case of linear and rotary encoders, they have been extensively used in sport sciences publications to predict the maximal dynamic strength of athletes from the Load-Velocity relationship [1, 2, 3], to evaluate reliability of other velocity and power measuring devices [4, 5] and measure concentric and eccentric power in inertial squat performance [6, 7] between other applications. Load cells have also been used extensively in multiple applications such as: measurement of maximum voluntary contraction or isometric strength (MVC) [8], the instantaneous and average force applied during concentric and eccentric contractions in inertial exercises [6] or simply measure forces from different nature such in the case of elastic bands [9]. The aim of the present work is to describe how to manufacture and reproduce a hardware-based device which can display and record signals from both sensors.

There are several products in the market which address this need, the pioneer product of the field is the MusclelabTM which interfaces different types of sensors with acquisition units that are connected to its specific software [https://www.musclelabsystem.com]. The other manufacturer which provides load cell and encoder data acquisition by interfacing these sensors with a computer is the Chronojump Boscosystem® [https://chronojump.org/]. The main difference of the present device in front of these two commercial products are the only open source hardware approach without the need of software for the acquisition and visualization as well as its completely reproduction at cost price and the battery powered approach which enables its use on any environment.

| Sport Analyzer | Chronojump | Musclelab
Load cell | Y | Y | Y
Linear encoder | Y | Y | Y
Rotary encoder | Y | Y | N
Battery powered | Y | N | N
Requires computer software | N | Y | Y
Open source software | Y | Y | N
Open source hardware | Y | N | N
GUI for data visualization | N | Y | Y
Cost (GBP) | 179.99 (parts) | 773.22 (from Chronojump) | 2,467.77 (from Simplifaster)

Problematic: Systems available are expensive or computer dependent and no hardware based

Table of the different commercial options

Figure with examples of figures of exercises to show applications

The relationship between power output and sport specificity was introduced by Bosco, Luhtanen and Komi in 1983 Velocity-Based Training

Table of capabilities

## Overall Implementation and Design

Describe how the hardware was implemented/created, with relevant details of the architecture and design, including general materials (Note: specific details on materials can be addressed in later section “Availability of materials and methods”). The use of diagrams and pictures of the assembled hardware is appropriate. Please also describe any variants and associated implementation differences.

Sport Analyzer is a programmable, Arduino compatible and battery powered device for simultaneous data collection and visualization of two important variables in sport sciences and rehabilitation which are force and velocity. The device accomplishes it by combining a load cell and optical incremental encoder data acquisition (Figure 1a).

System Architecture

The device has been designed to provide the visual image of a linear or rotary encoder and a load cell signals and at the same time acquire their data and save it inside a MicroSD card. It provides the simplicity of having one pushbutton to change the signal displayed and another to place a numeric label associated with the number of sample acquired. The device is battery operated using a regular 9V alkaline battery which also provides availability (Figure 1b).

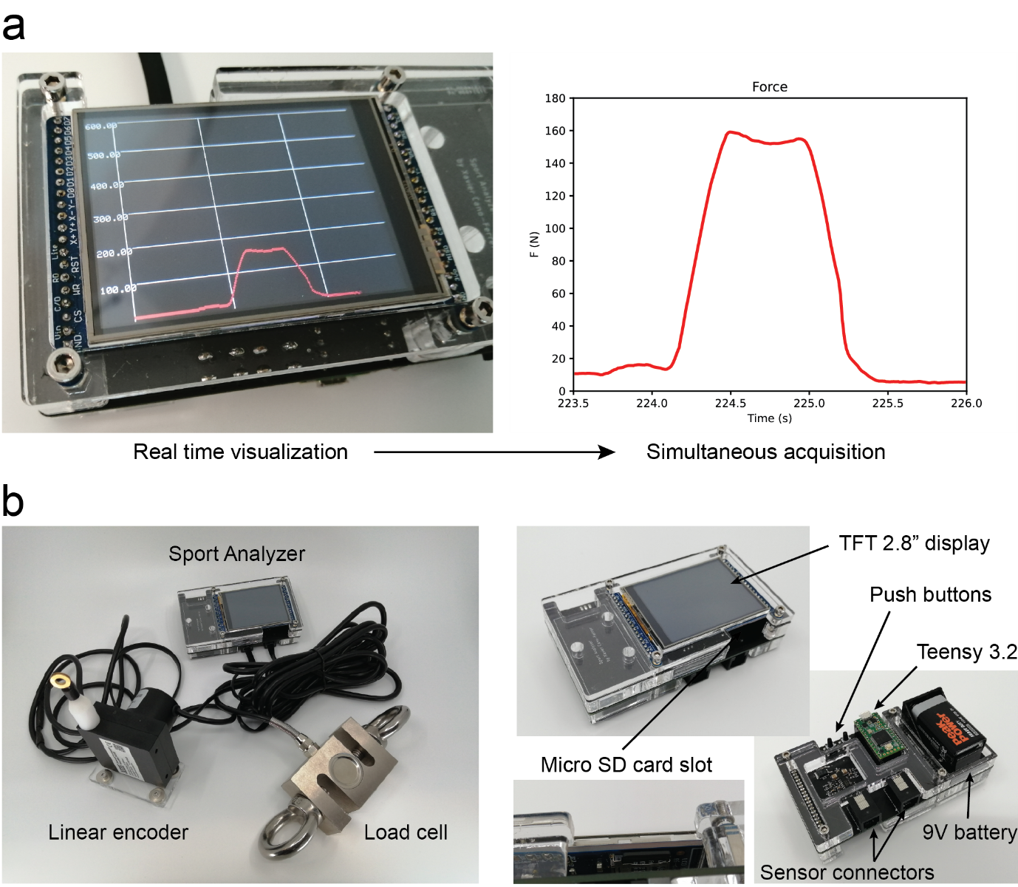
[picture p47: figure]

Figure 1: a. Sport Analyzer allows simultaneous data visualization and acquisition for its further analysis. The figure shows the same signal during the acquisition on the TFT display (left) and after the analysis in a plot from the data extracted from the txt. file (right). b. The device with the linear encoder and the load cell connected (left) and the main components of the device (right).

Electronics

The device main control unit is the Teensy 3.2 development board (Freescale Semiconductor MK20DX256). It has two RJ12 connectors which allow the connections for the Linear or rotary encoder and the load cell. It has a TFT 2.8” display (Adafruit 2.8" TFT LCD with Touchscreen Breakout Board with MicroSD Socket - ILI9341) which also has a MicroSD card socket where the device stores the data collected from the sensors in a txt. file. The device has two pushbuttons, the first one allows the user to switch from displaying the encoder signal (in color blue) and the load cell signal (in color red) on the TFT screen. The second pushbutton increments a counter to label the first column of data of the txt. file stored on the MicroSD card. The load cell conditioning signal is operated by a HX711 (24-Bit Analog-to-Digital Converter (ADC) for Weigh Scales, Avia Semiconductor). The optical incremental encoder signal admits 5V A, B and Z phases connection directly on the Teensy 3.2 pins, which are 5V tolerant. The device is powered using a regular 9V battery (Figure 2). The optical incremental encoder used in the present work is a Wisamic with 2400 pulses per revolution with a response frequency of (0-20) kHz and a maximum speed of 6000 rpm. On the other hand, the load cell is an S-type load cell which allows compression and tension forces measurement. The load cell main electrical properties are defined by the sensitivity of 2.0mV/V, repeatability of ±0.02(%F.S.), Input impedance of 350±10Ω, Linearity of ±0.02(%F.S.) and a measuring range of 4.9-4900 N.

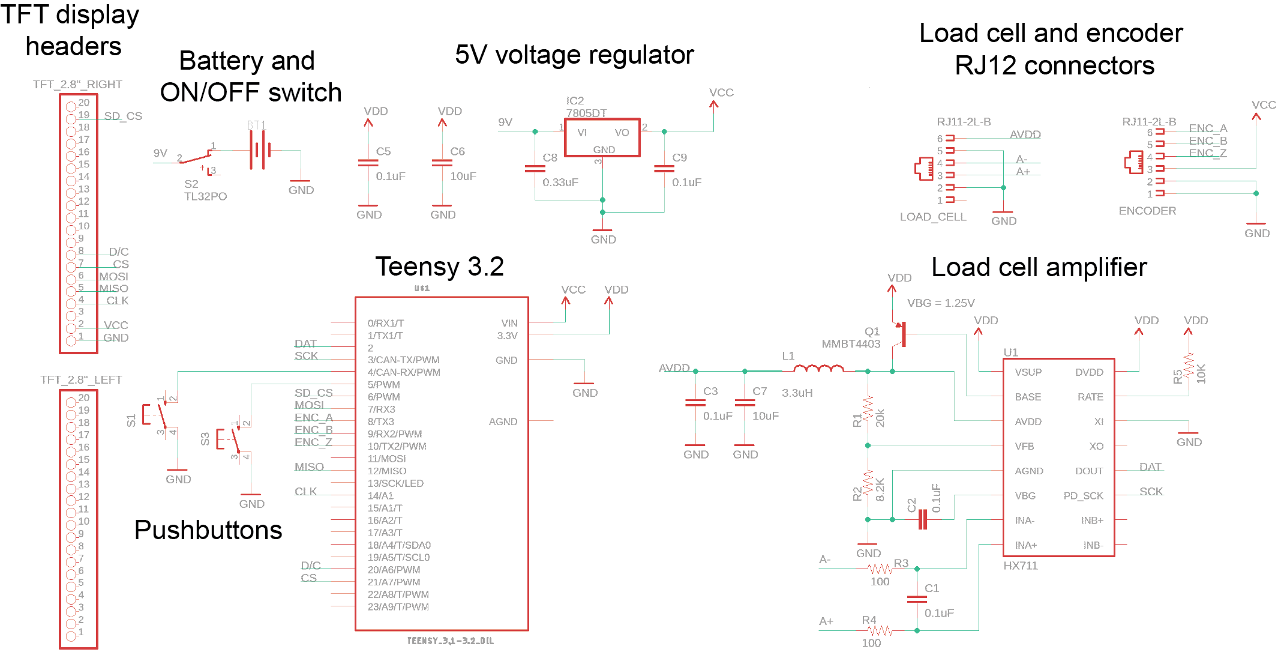
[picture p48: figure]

Figure 2: Electronic schematics of the device. Sport Analyzer schematic is composed by the Load cell amplifier circuit, the Teensy 3.2 development board, two pushbuttons, an ON/OFF switch, the two RJ12 sensor connectors, a 5V voltage regulator which converts the 9V of the battery and the TFT display pin headers.

Firmware

The firmware which is constantly running on the main loop function on the Teensy 3.2 is composed by its main file: Sport_Analayzer_1.0.ino which uses mainly six libraries: the SPI library [10], the ILI9341_t3 library [11], the font_Arial library [12], the Bounce library [13], the Encoder library [14], the SD library [15] and the HX711 library [16]. A part from the libraries, there are essential parts of the firmware that are based on the work of other authors, this functions are: the function that generates a graph for TFT displays [17] and the application we use to generate the code from the Sport Analyzer logo bitmap [18].

The main loop function of the firmware runs inside a three hundred samples for loop which is enough to fill the horizontal axis of the screen. For every iteration, a reading of the pushbuttons, load cell and encoder is performed and saved on the MicroSD card by calling a function called save_sd_card(). The velocity is computed every defined interval, which is by default 10 milliseconds and then the graph function is called displaying the desired signal. After the last iteration of the for loop the TFT display is restarted.

On the lines 21 and 46 v_max and F_max are the variables to change the maximum range of the vertical axis of velocity in the when displaying the encoder signal and the force when displaying the load cell signal. Two Boolean variables called linear_flag and rotational_flag enable the linear or the rotational conversion of the encoder pulses.

The firmware developed for the device is available on:

https://github.com/XaviCanoFerrer/Sport_Analyzer/tree/main/Firmware

Note: This is not meant to be an assembly instruction. Assembly instructions, detailed material lists, and construction files must be deposited in an appropriate repository (see Repositories document) and referenced in section “Build Details”.

### Subsections

We encourage the use of subsections to highlight the modular functionality of the design or to highlight different design achievements. These questions might help you find appropriate subsections: What parts of the hardware could be used as a component of another project or a variation of this hardware? What solutions do you find most noteworthy given your experiences during the design iterations? What separate actions does the hardware perform?

# (2) Quality control

## Safety

Describe all relevant safety issues or reference to a risk assessment if included in the hardware documentation. Detail what safety considerations have been included in the hardware design and how these features have been tested, including any official safety standards or criteria that were used in this assessment. If appropriate, discuss the wider context of use of the hardware and safety issues or risks that may arise in the use environment.

## Calibration

If the hardware is used for measurements, please detail here how the reliability of measurements, or other hardware properties that are relevant for measurements, has been quantified and explain the results. Be clear about the processes or procedures used to compare the hardware to a standard, as well as the description of the standard calibrated against.

Detail the general procedures in place for users to calibrate their hardware before or during use. What methods can be used to relate user generated data to data from other sources?

Note: Detailed instructions belong in documentation; here, provide insight into how and why the calibration is valid.

### Subsections

We encourage the use of subsections within all sections to increase clarity.

## General testing

In this section, details can be provided on the testing of hardware functionalities, that are not directly essential for precision operation of the hardware in the given context (which are in turn, where applicable, handled under Calibration), such as automated movements to position the hardware, repeatability of tool exchanges, recyclability, water-tightness, weight or other possibly relevant characteristics. We encourage the authors to characterise all appropriate functionalities of the hardware, if not already described elsewhere (add reference instead). The testing should define the safe/reliable limits in which the components can be operated (e.g. step size and repeatability of linear motion, force ranges, ratio of devices with leaks when built in a workshop, etc). This will enhance the usability of the hardware or method in other contexts.

| Value | Units
Sampling Frequency | 78 | Hz
Power consumption | 1.08 | W
Linear encoder resolution | 60 | µm
Load cell resolution | 0.1 | mN
Rotary encoder resolution | 2.6 | mrad
Maximum encoder measuring distance | 1.2 | m
Maximum load cell measuring force | 4.9 | kN

Again: Detailed instructions belong in documentation; here, provide a summary instead.

# (3) Application

## Use case(s)

Describe at least one example of an application of your hardware. This should include some evidence of output, e.g. data produced by the use of the device or a picture of other types of results. Outline how the quality control in the previous section enables the use of the hardware in this context. We encourage the inclusion of experiment results or the reference to a publication (published or to-be-published) where these results are detailed. We also encourage pointers to ongoing work.

Note: In the spirit of openness, we require authors to provide (or link to) datasets along with the submitted graphic representations. We do not impose arbitrary limits on inclusion of data so please include sufficient empirical detail and results to ensure your data can be easily verified, analysed and clearly interpreted by the wider scientific community.

### Subsections

We encourage the demonstration of different use cases, divided by sub-sections to guide the reader.

## Reuse potential and adaptability

Please describe in as much detail as possible the ways in which the hardware could be reused by other researchers both within and outside of your field. This should include the use cases for the hardware, and also details of how the hardware might be modified or extended (including how contributors should contact you) if appropriate. Refer to section “Ease of build” where necessary.

Please provide your thoughts on the adaptability of the hardware design. What tools and procedures would it require for other users to modify your design without your help in order to adapt them for foreseeable or even unforeseeable use.

Also you must include details of what support mechanisms there are in place for this hardware and software (even if there is no support or support community).

# (4) Build Details

## Availability of materials and methods

Summarise what materials have been used to construct the hardware and what methods to process the materials as well as the assembly. Provide more details or references where important materials or methods are non-standard, not globally available or produced only by one manufacturer.

## Ease of build

Have any measures been taken in the design to make the hardware easy to build for other users e.g. reduction of parts, features in the design to make the hardware assembly more reliable?

## Operating software and peripherals

If hardware requires software, details on the operating software and programming language - Please include minimum version compatibility. Additional system requirements, e.g. memory, disk space, processor, input or output devices.

If the hardware does not require software, detail any required supporting processes or protocols required for use.

## Dependencies

E.g. other hardware or software projects, modular components, libraries, frameworks, incl. minimum version compatibility. Explicitly state if dependencies are proprietary / closed source.

## Hardware documentation and files location:

Archive for hardware documentation and build files (required. See Repositories document for criteria, DocuBricks and alternative repositories.) Note: We require the inclusion of modifiable design files as well as a detailed documentation of the design rational of the hardware with assembly instructions. This will be assessed as part of the journal peer review process.

Name: The name of the archive

Persistent identifier: e.g. DOI, etc.

Licence: Open hardware license under which the documentation and files are licensed - see Essential author information for more information

Publisher: Name of the person who deposited the documentation

Date published: dd/mm/yy

Modifiable design files (if different from above)

Name: The name of the emulation environment

Persistent identifier: e.g. DOI, handle, PURL, etc.

Licence: Open license under which the software is licensed here

Publisher: Name of the person who deposited the documentation

Date published: dd/mm/yy

Software code repository (e.g. SourceForge, GitHub etc.) (required)

Name: The name of the code repository

Identifier: The identifier (or URI) used by the repository

Licence: Open license under which the software is licensed

Date published: dd/mm/yy

# (5) Discussion

## Conclusions

Conclusions, learned lessons from design iterations, learned lessons from use cases, summary of results.

## Future Work

Further work pursued by the authors or collaborators; known issues; suggestions for others to improve on the hardware design or testing,, given what you have learned from your design iterations.

## Paper author contributions

Task (e.g. design, assembly, use cases contribution, documentation, paper writing), contribution, author name.

## Acknowledgements

We thank Pau Gomez-Ferrer, Pier Sietti, Artur Lopez, Rainiero for the feedback of the functionality of the device.

Please add any relevant acknowledgements to anyone else who supported the project in which the hardware was created, but did not work directly on the hardware itself.

Please list anyone who helped to create the hardware and software (who may also not be an author of this paper), including their roles and affiliations.

## Funding statement

If the hardware resulted from funded research please give the funder and grant number.

## Competing interests

If any of the authors have any competing interests then these must be declared. The authors’ initials should be used to denote differing competing interests. For example: “BH has minority shares in [company name], which part funded the research grant for this project. All other authors have no competing interests." Or “BH is selling kits and parts connected to the here presented hardware via platform XX. A fundraising via Crowdfunding platform YY is planned to start commercialisation.”

If there are no competing interests, please add the statement:

“The authors declare that they have no competing interests.”

The authors declare that they have no competing interests.

## References

Please enter references in the Harvard style and include a DOI where available, citing them in the text with a number in square brackets, e.g.

[1] Bazuelo-Ruiz B, Padial P, García-Ramos A, Morales-Artacho AJ, Miranda MT, Feriche B. Predicting Maximal Dynamic Strength From the Load-Velocity Relationship in Squat Exercise. J Strength Cond Res. 2015 Jul;29(7):1999-2005. doi: 10.1519/JSC.0000000000000821. PMID: 25881572.

[2] Banyard, Harry G.; Nosaka, Kazunori; Haff, G. Gregory Reliability and Validity of the Load–Velocity Relationship to Predict the 1RM Back Squat, Journal of Strength and Conditioning Research: July 2017 - Volume 31 - Issue 7 - p 1897-1904 doi: 10.1519/JSC.0000000000001657

[3] Bosquet L, Porta-Benache J, Blais J. Validity of a Commercial Linear Encoder to Estimate Bench Press 1 RM from the Force-Velocity Relationship. J Sports Sci Med. 2010 Sep 1;9(3):459-63. PMID: 24149641; PMCID: PMC3761713.

[4] van den Tillaar R, Ball N. Validity and Reliability of Kinematics Measured with PUSH Band vs. Linear Encoder in Bench Press and Push-Ups. Sports (Basel). 2019 Sep 10;7(9):207. doi: 10.3390/sports7090207. PMID: 31509960; PMCID: PMC6784224.

[5] Ferro A, Floría P, Villacieros J, Muñoz-López A. Maximum velocity during loaded countermovement jumps obtained with an accelerometer, linear encoder and force platform: A comparison of technologies. J Biomech. 2019 Oct 11;95:109281. doi: 10.1016/j.jbiomech.2019.07.025. Epub 2019 Jul 31. PMID: 31471113.

[6] Illera-Domínguez V, Nuell S, Carmona G, Padullés JM, Padullés X, Lloret M, Cussó R, Alomar X, Cadefau JA. Early Functional and Morphological Muscle Adaptations During Short-Term Inertial-Squat Training. Front Physiol. 2018 Sep 10;9:1265. doi: 10.3389/fphys.2018.01265. PMID: 30246805; PMCID: PMC6139363.

[7] Lindemann U, Farahmand P, Klenk J, Blatzonis K, Becker C. Validity of linear encoder measurement of sit-to-stand performance power in older people. Physiotherapy. 2015 Sep;101(3):298-302. doi: 10.1016/j.physio.2014.12.005. Epub 2015 Mar 2. PMID: 25796540.

[8] Macaluso A, De Vito G. Comparison between young and older women in explosive power output and its determinants during a single leg-press action after optimisation of load. Eur J Appl Physiol. 2003 Nov;90(5-6):458-63. doi: 10.1007/s00421-003-0866-7. Epub 2003 Jul 19. PMID: 12883896.

[9] Fuentes AD, Smith CJ, Shoepe TC. Loading Patterns of Rubber-Based Resistance Bands across Distributors. Sports (Basel). 2019 Jan 16;7(1):21. doi: 10.3390/sports7010021. PMID: 30654430; PMCID: PMC6358948.

[10] Paul Stoffregen, “SPI library for Teensy & Arduino IDE” https://github.com/PaulStoffregen/SPI

[11] Paul Stoffregen, https://github.com/PaulStoffregen/ILI9341_t3/blob/master/font_Arial.h

[12] Paul Stoffregen, “Optimized ILI9341 TFT Library” https://github.com/PaulStoffregen/ILI9341_t3

[13] Thomas O Fredericks, “Debouncing library for Arduino and Wiring” https://github.com/thomasfredericks/Bounce2

[14] Paul Stoffregen, “Quadrature Encoder Library for Arduino” https://github.com/PaulStoffregen/Encoder

[15] Paul Stoffregen, https://github.com/PaulStoffregen/SD

[16] Bogdan Necula, “An Arduino library to interface the Avia Semiconductor HX711 24-Bit Analog-to-Digital Converter (ADC) for Weight Scales.” https://github.com/bogde/HX711

[17] Kris Kasprzak, “Functions to draw graphs on LCD” https://github.com/KrisKasprzak/GraphingFunction/blob/master/Graph.ino

[18] Jasper van Loenen, “” http://javl.github.io/image2cpp/

[] Bosco C, Luhtanen P, Komi PV. A simple method for measurement of mechanical power in jumping. Eur J Appl Physiol Occup Physiol. 1983;50(2):273-82. doi: 10.1007/BF00422166. PMID: 6681758.

Martin, L 2010 Bombs, bodies and biopolitics: Securitizing the subject at airport security. Social and Cultural Geography, 11(1): 17-34. DOI: http://dx.doi.org/10.1080/14649360903414585

NOTE: Please include DOIs for all journal articles where possible.

# Copyright notice

Authors who publish with this journal agree to the following terms:

Authors retain copyright and grant the journal right of first publication with the work simultaneously licensed under a (http://creativecommons.org/licenses/by/3.0/)Creative Commons Attribution License (http://creativecommons.org/licenses/by/3.0/) that allows others to share the work with an acknowledgement of the work's authorship and initial publication in this journal.

Authors are able to enter into separate, additional contractual arrangements for the non-exclusive distribution of the journal's published version of the work (e.g., post it to an institutional repository or publish it in a book), with an acknowledgement of its initial publication in this journal.

By submitting this paper you agree to the terms of this Copyright Notice, which will apply to this submission if and when it is published by this journal.

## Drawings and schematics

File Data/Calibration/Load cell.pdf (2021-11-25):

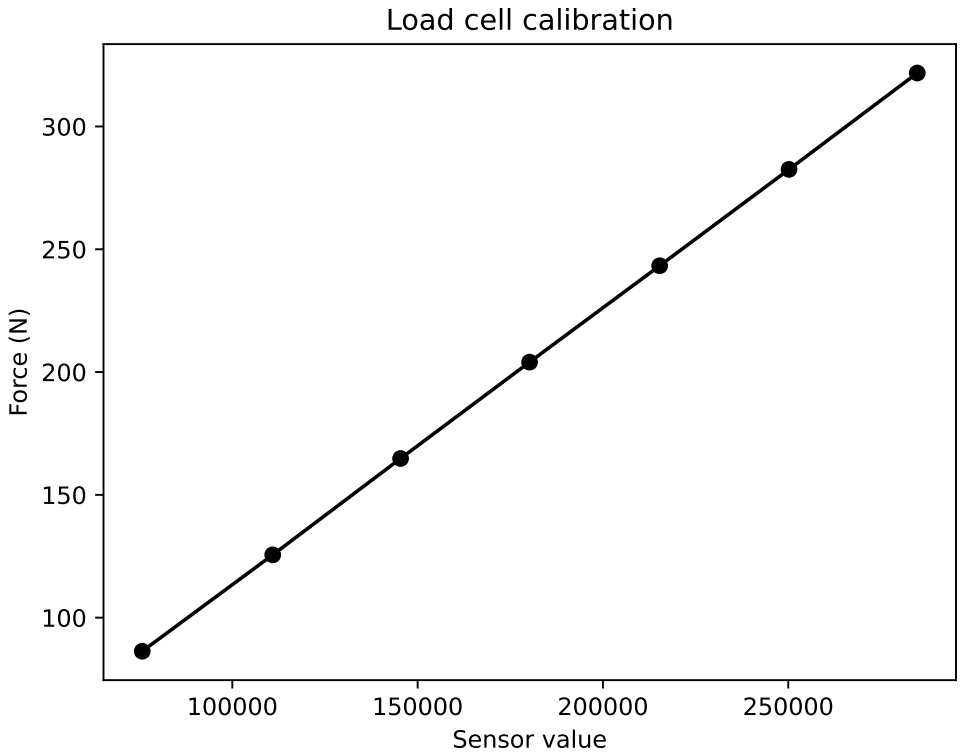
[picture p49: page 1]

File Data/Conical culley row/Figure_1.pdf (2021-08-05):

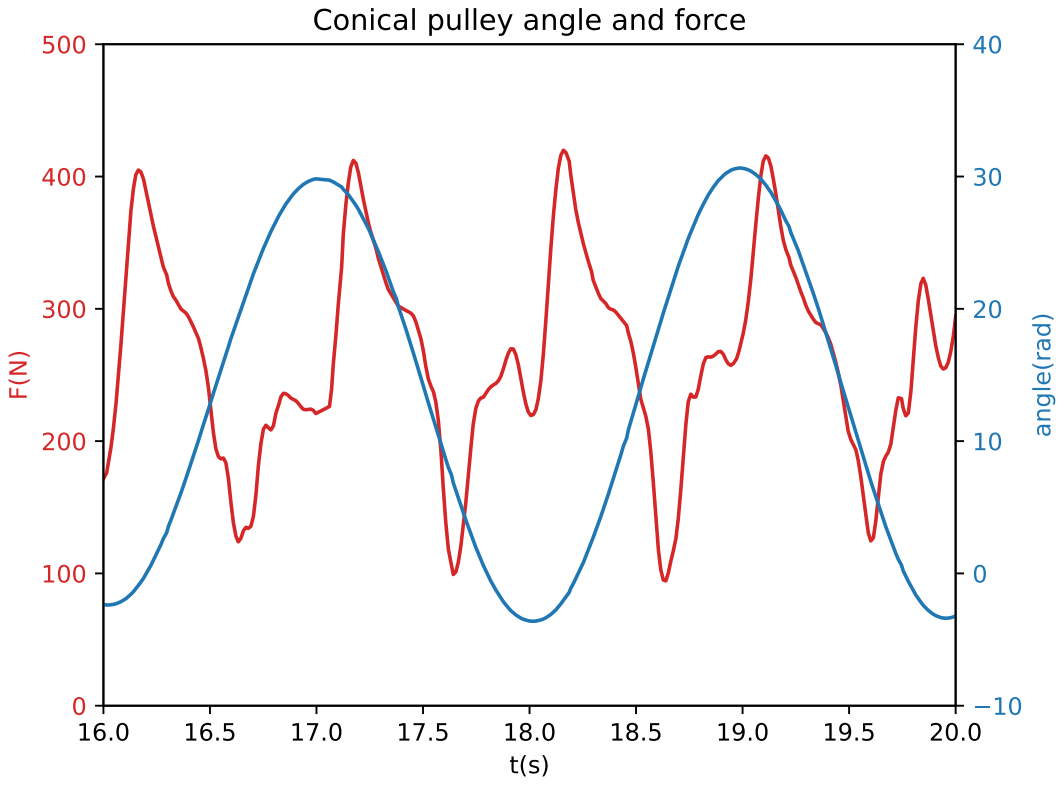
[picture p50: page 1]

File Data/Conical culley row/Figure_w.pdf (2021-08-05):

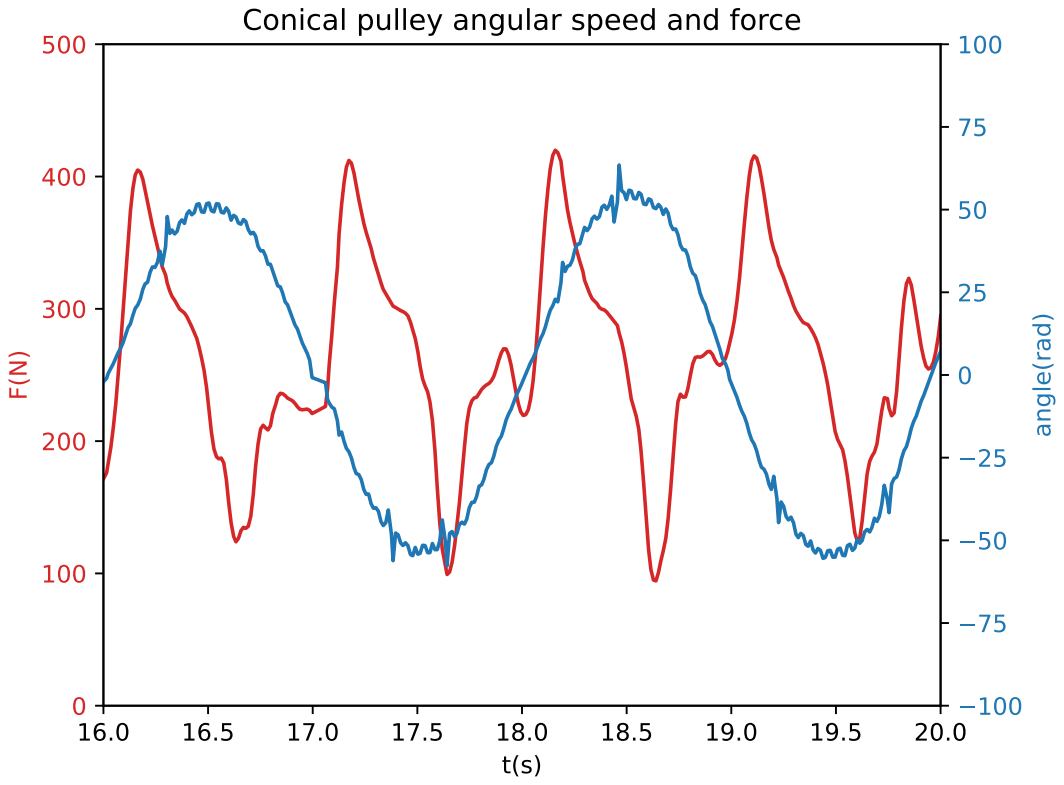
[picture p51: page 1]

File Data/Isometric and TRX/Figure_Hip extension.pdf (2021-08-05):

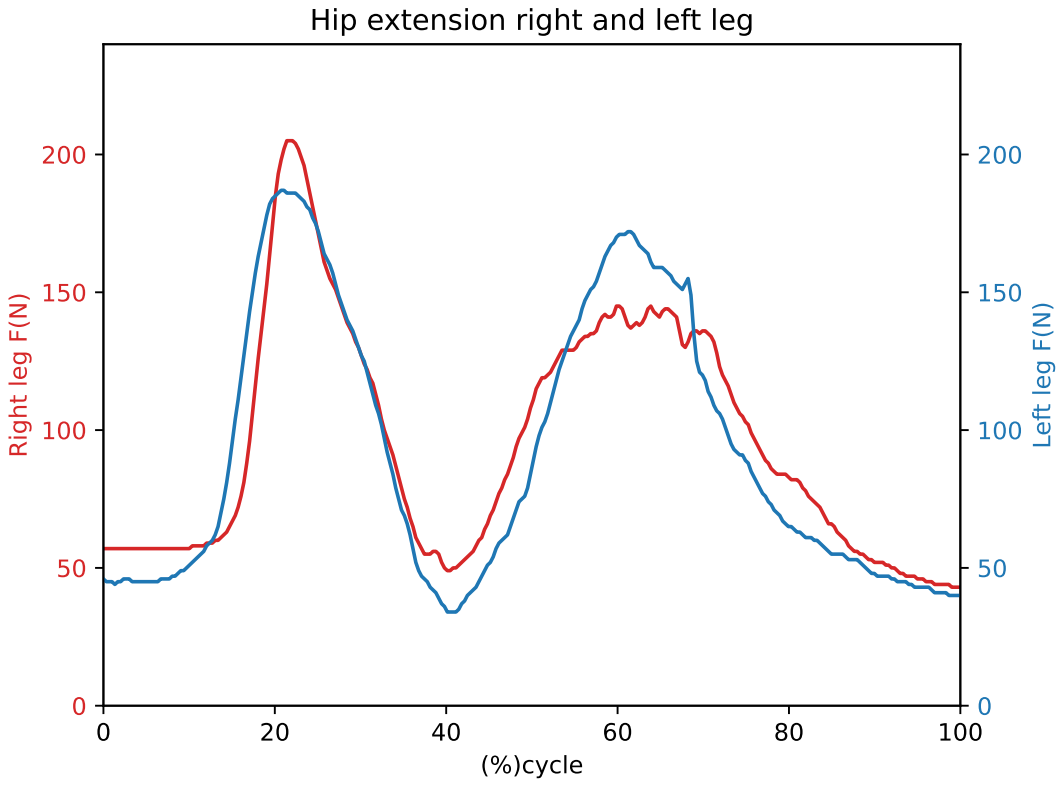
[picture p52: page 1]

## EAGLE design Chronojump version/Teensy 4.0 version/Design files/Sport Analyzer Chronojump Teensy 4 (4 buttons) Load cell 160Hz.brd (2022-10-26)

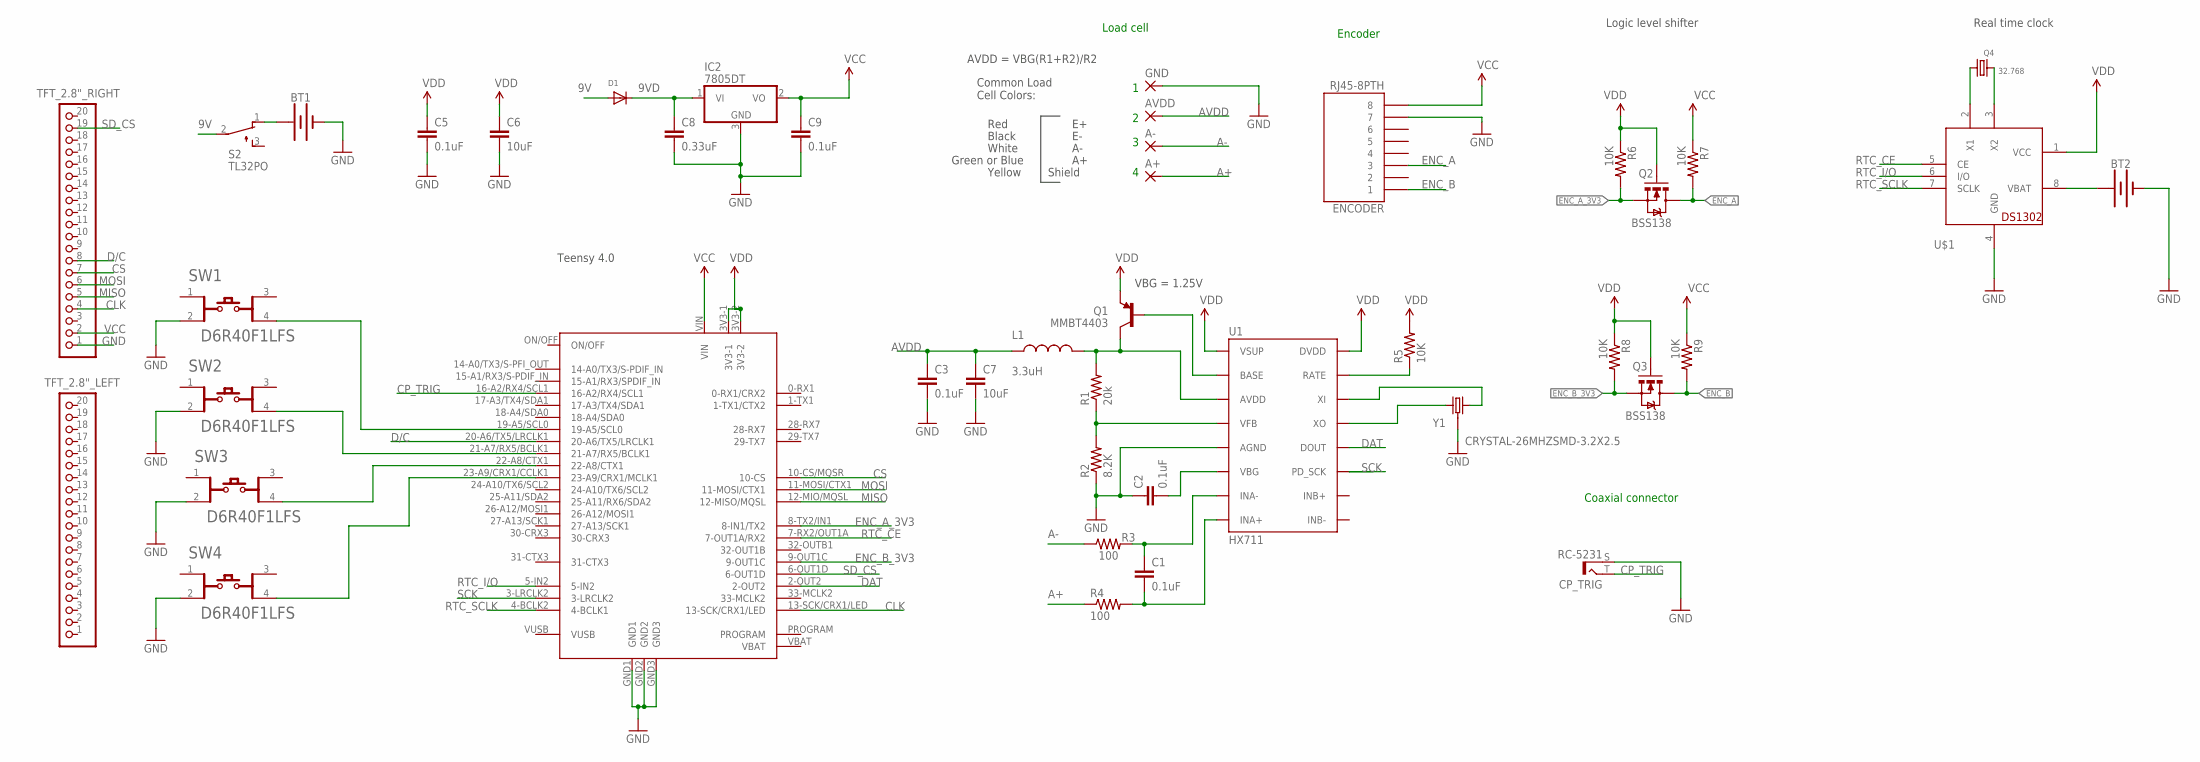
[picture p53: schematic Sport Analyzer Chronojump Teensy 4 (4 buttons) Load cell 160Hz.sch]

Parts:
A+: 3,81/1,4
A-: 3,81/1,4
AVDD: 3,81/1,4
BT1: BATTERY-9V; BATTCON_9V
BT2: BATTERY-12MM_SMD; BATTCON_12MM
C1, C2, C3, C5, C9: 0.1uF; 0603-CAP
C6, C7: 10uF; 1210
C8: 0.33uF; 0603-CAP
CP_TRIG: RC-5231
D1: DIODESOD-123; SOD-123
ENCODER: RJ45-8PTH; RJ45-8
GND: 3,81/1,4
IC2: 7805DT; TO252
L1: 3.3uH; 0805
Q1: MMBT4403; SOT23-3
Q2, Q3: BSS138; SOT23-3
Q4: 32.768; CRYSTAL_8X3.8
R1: 20k; 0603-RES
R2: 8.2K; 0603-RES
R3, R4: 100; 0603-RES
R5, R6, R7, R8, R9: 10K; 0603-RES
S2: TL32PO; TL3XPO
SW1, SW2, SW3, SW4: C&K_COMPONENTS_D6R40F1LFSC&K_COMPONENTS_D6R40F1LF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; C&K_COMPONENTS_D6R40F1LFS_0
TFT_2.8"_LEFT, TFT_2.8"_RIGHT: PINHD-1X20; 1X20
U1: HX711; SO16
U$1: DS1302; DIL08-ROUND
U$2: TEENSY40
Y1: CRYSTAL-26MHZSMD-3.2X2.5; CRYSTAL-SMD-3.2X2.5MM

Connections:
9V: D1.A, S2.2
9VD: C8.1, D1.C, IC2.1 (VI)
A+: A+.1, R4.1
A-: A-.1, R3.1
AVDD: AVDD.1, C3.1, C7.1, L1.1
CLK: TFT_2.8"_RIGHT.4, U$2.13-SCK/CRX1/LED
CP_TRIG: CP_TRIG.T, U$2.16-A2/RX4/SCL1
CS: TFT_2.8"_RIGHT.7, U$2.10-CS/MQSR (10-CS)
D/C: TFT_2.8"_RIGHT.8, U$2.20-A6/TX5/LRCLK1
DAT: U1.12 (DOUT), U$2.2-OUT2
ENC_A: ENCODER.3, Q2.3 (D), R7.2
ENC_A_3V3: Q2.2 (S), R6.2, U$2.8-TX2/IN1 (8-IN1/TX2)
ENC_B: ENCODER.1, Q3.3 (D), R9.2
ENC_B_3V3: Q3.2 (S), R8.2, U$2.9-OUT1C
GND: BT1.-, BT2.GND (-), C2.1, C3.2, C5.2, C6.2, C7.2, C8.2, C9.2, CP_TRIG.S, ENCODER.7, GND.1, IC2.3 (GND), R2.1, SW1.2, SW2.2, SW3.2, SW4.2, TFT_2.8"_RIGHT.1, U1.5 (AGND), U$1.4 (GND), U$2.GND1, U$2.GND2, U$2.GND3, Y1.2 (GND), Y1.4 (GND)
MISO: TFT_2.8"_RIGHT.5, U$2.12-MIO/MQSL (12-MISO/MQSL)
MOSI: TFT_2.8"_RIGHT.6, U$2.11-MOSI/CTX1
unnamed: R5.1, U1.15 (RATE)
unnamed: C1.1, R3.2, U1.7 (INA-)
unnamed: C1.2, R4.2, U1.8 (INA+)
unnamed: Q1.1 (B), U1.2 (BASE)
unnamed: L1.2, Q1.3 (C), R1.2, U1.3 (AVDD)
unnamed: R1.1, R2.2, U1.4 (VFB)
unnamed: C2.2, U1.6 (VBG)
unnamed: Q4.P$4 (2), U$1.2 (X1)
unnamed: Q4.P$1 (1), U$1.3 (X2)
unnamed: SW1.4, U$2.19-A5/SCL0
unnamed: SW2.4, U$2.21-A7/RX5/BCLK1
unnamed: SW3.4, U$2.22-A8/CTX1
unnamed: SW4.4, U$2.23-A9/CRX1/CCLK1 (23-A9/CRX1/MCLK1)
unnamed: U1.13 (XO), Y1.1
unnamed: U1.14 (XI), Y1.3 (2)
unnamed: BT2.PWR@1 (+), U$1.8 (VBAT)
unnamed: BT1.+, S2.1 (O)
RTC_CE: U$1.5 (CE), U$2.7-RX2/OUT1A (7-OUT1A/RX2)
RTC_I/O: U$1.6 (I/O), U$2.5-IN2
RTC_SCLK: U$1.7 (SCLK), U$2.4-BCLK2 (4-BCLK1)
SCK: U1.11 (PD_SCK), U$2.3-LRCLK2
SD_CS: TFT_2.8"_RIGHT.19, U$2.6-OUT1D
VCC: C9.1, ENCODER.8, IC2.2 (VO), R7.1, R9.1, TFT_2.8"_RIGHT.2, U$2.VIN
VDD: C5.1, C6.1, Q1.2 (E), Q2.1 (G), Q3.1 (G), R5.2, R6.1, R8.1, U1.1 (VSUP), U1.16 (DVDD), U$1.1 (VCC), U$2.3V3-1, U$2.3V3-2

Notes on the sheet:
VBG = 1.25V
AVDD = VBG(R1+R2)/R2
Red
Black
White
Green or Blue
Common Load Cell Colors:
Shield
Yellow
Encoder
Coaxial connector
Load cell
Logic level shifter
Teensy 4.0
Real time clock

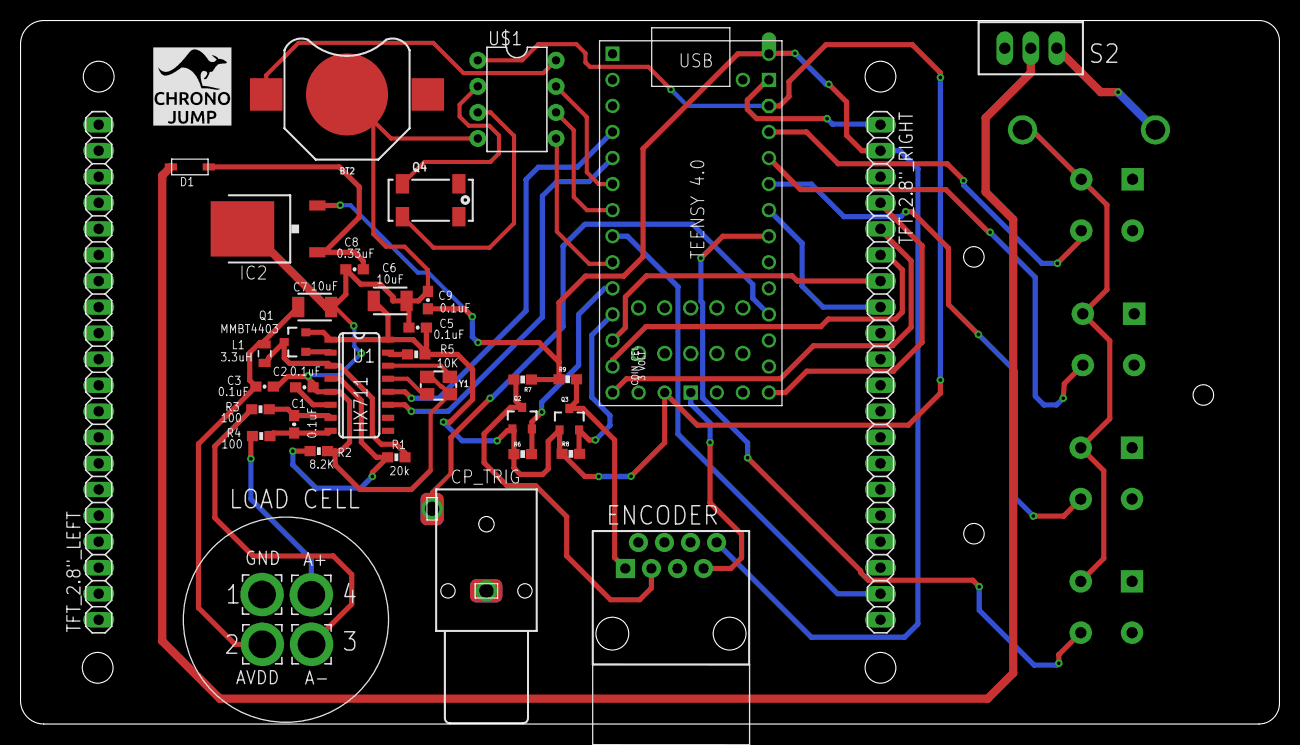
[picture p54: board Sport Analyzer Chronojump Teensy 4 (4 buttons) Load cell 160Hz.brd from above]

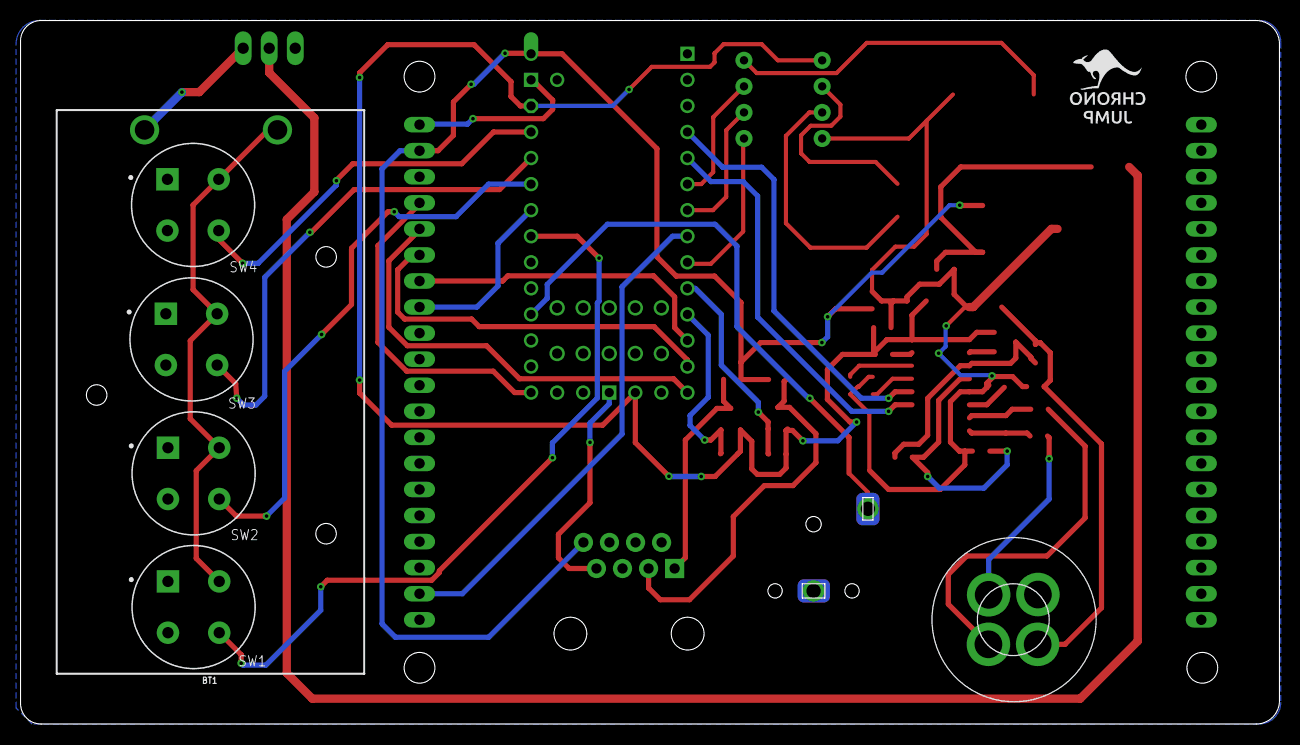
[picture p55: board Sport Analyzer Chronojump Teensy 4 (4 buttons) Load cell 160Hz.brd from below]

Board: 2 copper layers, 122.7 x 68.6 mm, 43 parts (5 on the bottom side), 41 nets.

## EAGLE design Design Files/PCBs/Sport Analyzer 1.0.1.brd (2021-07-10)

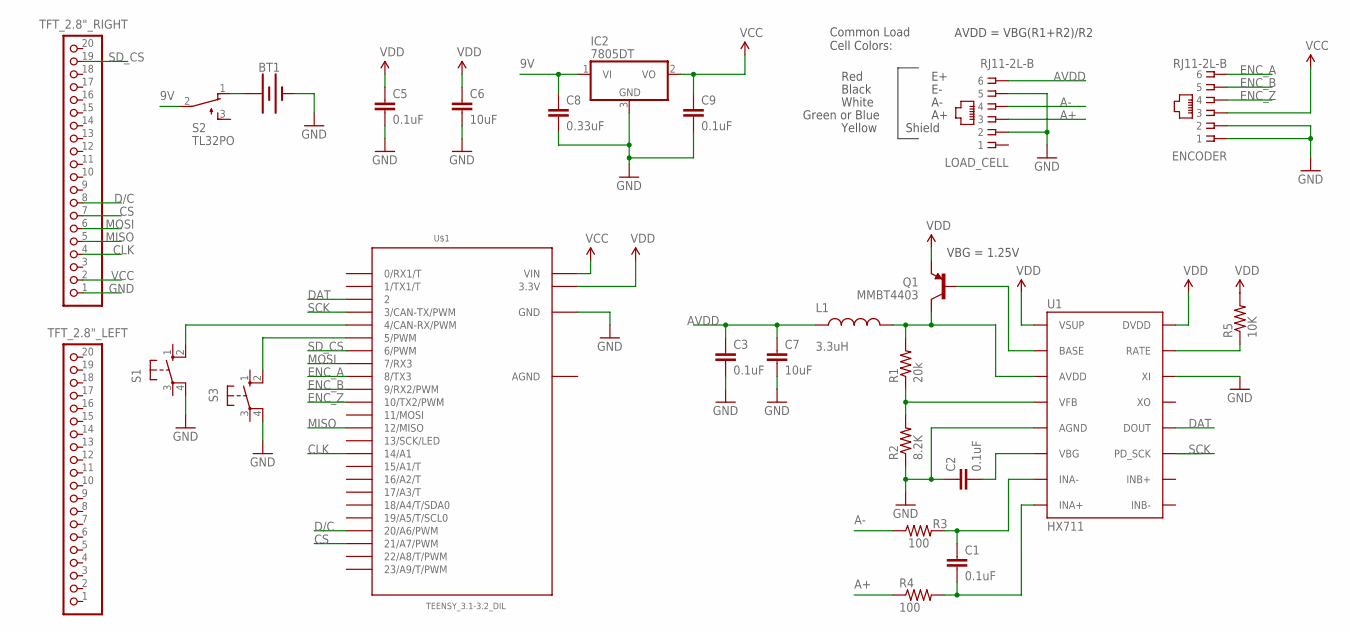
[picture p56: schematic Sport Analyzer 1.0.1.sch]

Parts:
BT1: BATTERY-9V; BATTCON_9V
C1, C2, C3, C5, C9: 0.1uF; 0603-CAP
C6, C7: 10uF; 1210
C8: 0.33uF; 0603-CAP
ENCODER: RJ11-2L-B; RJ11-NO_SHIELD
IC2: 7805DT; TO252
L1: 3.3uH; 0805
LOAD_CELL: RJ11-2L-B; RJ11-NO_SHIELD
Q1: MMBT4403; SOT23-3
R1: 20k; 0603-RES
R2: 8.2K; 0603-RES
R3, R4: 100; 0603-RES
R5: 10K; 0603-RES
S1, S3: 10-XX; B3F-10XX
S2: TL32PO; TL3XPO
TFT_2.8"_LEFT, TFT_2.8"_RIGHT: PINHD-1X20; 1X20
U1: HX711; SO16
U$1: TEENSY_3.1-3.2_DIL; TEENSY_3.0-3.2&LC_DIL

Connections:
9V: C8.1, IC2.1 (VI), S2.2
A+: LOAD_CELL.3, R4.1
A-: LOAD_CELL.4, R3.1
AGND: U$1.AGND
AVDD: C3.1, C7.1, L1.1, LOAD_CELL.6
CLK: TFT_2.8"_RIGHT.4, U$1.14/A0 (14/A1)
CS: TFT_2.8"_RIGHT.7, U$1.21/A7 (21/A7/PWM)
D/C: TFT_2.8"_RIGHT.8, U$1.20/A6 (20/A6/PWM)
DAT: U1.12 (DOUT), U$1.2
ENC_A: ENCODER.6, U$1.8 (8/TX3)
ENC_B: ENCODER.5, U$1.9 (9/RX2/PWM)
ENC_Z: ENCODER.4, U$1.10 (10/TX2/PWM)
GND: BT1.-, C2.1, C3.2, C5.2, C6.2, C7.2, C8.2, C9.2, ENCODER.1, ENCODER.2, IC2.3 (GND), LOAD_CELL.2, LOAD_CELL.5, R2.1, S1.4 (P1), S3.4 (P1), TFT_2.8"_RIGHT.1, U1.5 (AGND), U1.14 (XI), U$1.GND
MISO: TFT_2.8"_RIGHT.5, U$1.12 (12/MISO)
MOSI: TFT_2.8"_RIGHT.6, U$1.7 (7/RX3)
unnamed: R5.1, U1.15 (RATE)
unnamed: C1.1, R3.2, U1.7 (INA-)
unnamed: C1.2, R4.2, U1.8 (INA+)
unnamed: Q1.1 (B), U1.2 (BASE)
unnamed: L1.2, Q1.3 (C), R1.2, U1.3 (AVDD)
unnamed: R1.1, R2.2, U1.4 (VFB)
unnamed: C2.2, U1.6 (VBG)
unnamed: S1.2 (S1), U$1.4 (4/CAN-RX/PWM)
unnamed: S3.2 (S1), U$1.5 (5/PWM)
unnamed: BT1.+, S2.1 (O)
SCK: U1.11 (PD_SCK), U$1.3 (3/CAN-TX/PWM)
SD_CS: TFT_2.8"_RIGHT.19, U$1.6 (6/PWM)
VCC: C9.1, ENCODER.3, IC2.2 (VO), TFT_2.8"_RIGHT.2, U$1.VIN
VDD: C5.1, C6.1, Q1.2 (E), R5.2, U1.1 (VSUP), U1.16 (DVDD), U$1.3.3V

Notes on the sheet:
VBG = 1.25V
AVDD = VBG(R1+R2)/R2
Red
Black
White
Green or Blue
Common Load Cell Colors:
Shield
Yellow

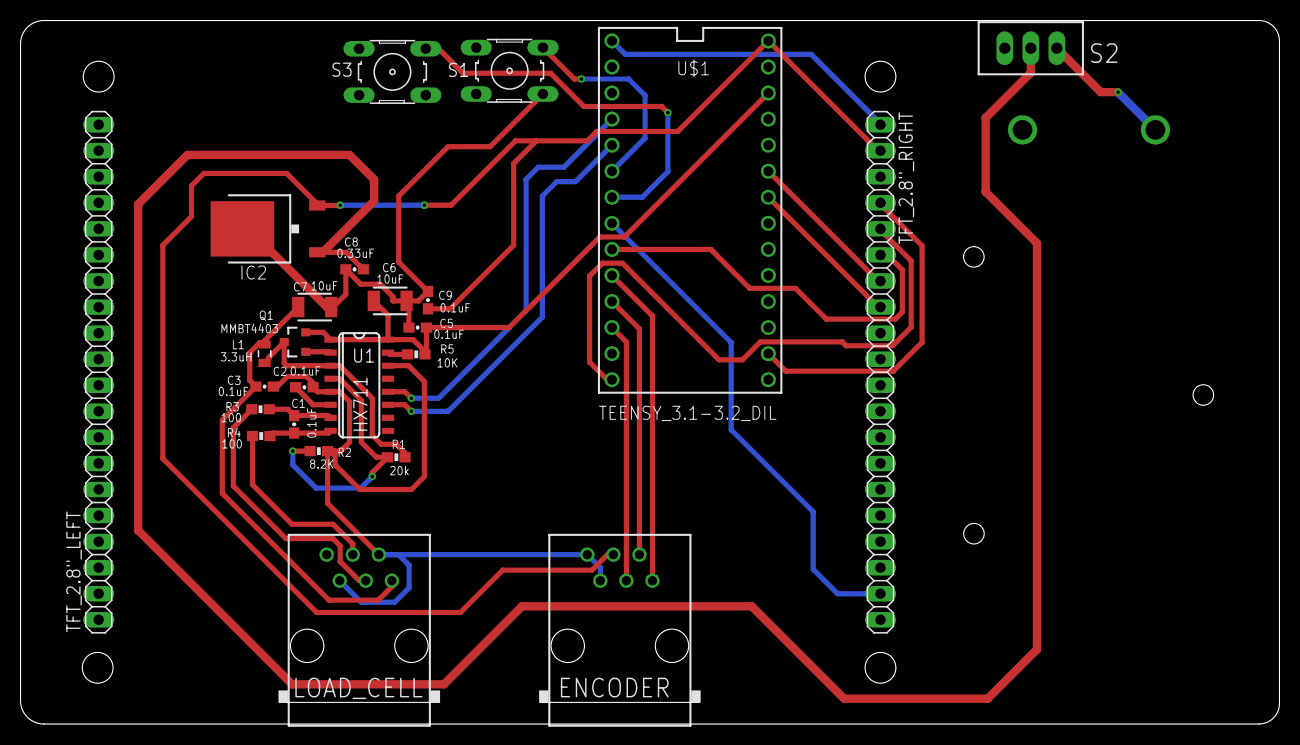
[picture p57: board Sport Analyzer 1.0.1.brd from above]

Board: 2 copper layers, 122.7 x 68.6 mm, 26 parts (1 on the bottom side), 28 nets.

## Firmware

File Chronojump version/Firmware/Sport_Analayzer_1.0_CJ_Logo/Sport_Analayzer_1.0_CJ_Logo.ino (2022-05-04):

/*
  ----------------------------------------------------------------------------

  This file is part of the Sport analyzer repository
  Written by Xavier Cano-Ferrer

  ----------------------------------------------------------------------------

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
*/

#include "SPI.h"
#include "ILI9341_t3.h"
#include "font_Arial.h"
#include "HX711.h"
#include <Bounce.h>
#include <Encoder.h>
#include <SD.h>

//Encoder variables
Encoder encoder(8,9);
float s = 0;
float s_i = 0;
float v = 0;
elapsedMillis Interval = 0;
unsigned long milliseconds = 10;
const float ppr = 2400; // Encoder Pulses per revolution
const float dpr = 360; // Degrees per revolution
const float mmpp = 0.06; //mm per pulse
bool rotatiional_flag = false;
bool linear_flag = true;
int v_max = 400; // max velocity on y axis of the display

// Button variables
const int buttonPin = 4;
Bounce pushbutton = Bounce(buttonPin, 10);  // 10 ms debounce
byte previousState = HIGH;         // what state was the button last time
unsigned int count = 1;            // how many times has it changed to low
unsigned long countAt = 0;         // when count changed
unsigned int countPrinted = 0;     // last count printed
bool state = LOW;
bool previous_state;

//Second button to generate new subjects
const int buttonPin_2 = 5;
Bounce pushbutton_2 = Bounce(buttonPin_2, 10);  // 10 ms debounce

//Maximum number of file names
char fileName[100];

//Load cell variables
HX711 scale;
const int LOADCELL_DOUT_PIN = 2;
const int LOADCELL_SCK_PIN = 3;
long load_cell_reading;
float F;
const int F_max = 600; //Maximum force on y axis of the display 

// Display variables
const int chipSelect = 6;
#define TFT_DC      20
#define TFT_CS      21
#define TFT_RST    255  // 255 = unused, connect to 3.3V
#define TFT_MOSI     7
#define TFT_SCLK    14
#define TFT_MISO    12
ILI9341_t3 tft = ILI9341_t3(TFT_CS, TFT_DC, TFT_RST, TFT_MOSI, TFT_SCLK, TFT_MISO);

// Display 16-bit color values:
#define BLUE      0x001F
#define TEAL      0x0438
#define GREEN     0x07E0
#define CYAN      0x07FF
#define RED       0xF800
#define MAGENTA   0xF81F
#define YELLOW    0xFFE0
#define ORANGE    0xFC00
#define PINK      0xF81F
#define PURPLE    0x8010
#define GREY      0xC618
#define WHITE     0xFFFF
#define BLACK     0x0000

boolean display1 = true;
double ox , oy ;
double x, y;

const unsigned char logo [] PROGMEM = {
  
0xff, 0xff, 0xff, 0xff, 0xff, 0xff, 0xff, 0xff, 0xff, 0xff, 0xff, 0xff, 0xff, 0xff, 0xff, 0xff, 
  0xff, 0xff, 0xff, 0xff, 0xff, 0xff, 0xff, 0xff, 0xff, 0xff, 0xff, 0xff, 0xff, 0xff, 0xff, 0xff, 
  0xff, 0xff, 0xff, 0xff, 0xff, 0xff, 0xff, 0xff, 0xff, 0xff, 0xff, 0xff, 0xff, 0xff, 0xff, 0xff, 
  0xff, 0xff, 0xff, 0xff, 0xff, 0xff, 0xff, 0xff, 0xff, 0xff, 0xff, 0xff, 0xff, 0xff, 0xff, 0xff, 
  0xff, 0xff, 0xff, 0xff, 0xff, 0xff, 0xff, 0xff, 0xff, 0xff, 0xff, 0xff, 0xff, 0xff, 0xff, 0xff, 
  0xff, 0xff, 0xff, 0xff, 0xff, 0xff, 0xff, 0xff, 0xff, 0xff, 0xff, 0xff, 0xff, 0xff, 0xff, 0xff, 
  0xff, 0xff, 0xff, 0xff, 0xff, 0xff, 0xff, 0xff, 0xff, 0xff, 0xff, 0xff, 0xff, 0xff, 0xff, 0xff, 
  0xff, 0xff, 0xff, 0xff, 0xff, 0xff, 0xff, 0xff, 0xff, 0xff, 0xff, 0xff, 0xff, 0xff, 0xff, 0xff, 
  0xff, 0xff, 0xff, 0xff, 0xff, 0xff, 0xff, 0xff, 0xff, 0xff, 0xff, 0xff, 0xff, 0xff, 0xff, 0xff, 
  0xff, 0xff, 0xff, 0xff, 0xff, 0xff, 0xff, 0xff, 0xff, 0xff, 0xff, 0xff, 0xff, 0xff, 0xff, 0xff, 
  0xff, 0xff, 0xff, 0xff, 0xff, 0xff, 0xff, 0xff, 0xff, 0xff, 0xff, 0xff, 0xff, 0xff, 0xff, 0xff, 
  0xff, 0xff, 0xff, 0xff, 0xff, 0xff, 0xff, 0xff, 0xff, 0xff, 0xff, 0xff, 0xff, 0xff, 0xff, 0xff, 
  0xff, 0xff, 0xff, 0xff, 0xff, 0xff, 0xff, 0xff, 0xff, 0xff, 0xff, 0xff, 0xff, 0xff, 0xff, 0xff, 
  0xff, 0xff, 0xff, 0xff, 0xff, 0xff, 0xff, 0xff, 0xff, 0xff, 0xff, 0xff, 0xff, 0xff, 0xff, 0xff, 
  0xff, 0xff, 0xff, 0xff, 0xff, 0xff, 0xff, 0xff, 0xff, 0xff, 0xff, 0xff, 0xff, 0xff, 0xff, 0xff, 
  0xff, 0xff, 0xff, 0xff, 0xff, 0xff, 0xff, 0xff, 0xff, 0xff, 0xff, 0xff, 0xff, 0xff, 0xff, 0xff, 
  0xff, 0xff, 0xff, 0xff, 0xff, 0xff, 0xff, 0xff, 0xff, 0xff, 0xff, 0xff, 0xff, 0xff, 0xff, 0xff, 
  0xff, 0xff, 0xff, 0xff, 0xff, 0xff, 0xff, 0xff, 0xff, 0xff, 0xff, 0xff, 0xff, 0xff, 0xff, 0xff, 
  0xff, 0xff, 0xff, 0xff, 0xff, 0xff, 0xff, 0xff, 0xff, 0xff, 0xff, 0xff, 0xff, 0xff, 0xff, 0xff, 
  0xff, 0xff, 0xff, 0xff, 0xff, 0xff, 0xff, 0xff, 0xff, 0xff, 0xff, 0xff, 0xff, 0xff, 0xff, 0xff, 
  0xff, 0xff, 0xff, 0xff, 0xff, 0xff, 0xff, 0xff, 0xff, 0xff, 0xff, 0xff, 0xff, 0xff, 0xff, 0xff, 
  0xff, 0xff, 0xff, 0xff, 0xff, 0xff, 0xff, 0xff, 0xff, 0xff, 0xff, 0xff, 0xff, 0xff, 0xff, 0xff, 
  0xff, 0xff, 0xff, 0xff, 0xff, 0xff, 0xff, 0xff, 0xff, 0xff, 0xff, 0xff, 0xff, 0xff, 0xff, 0xff, 
  0xff, 0xff, 0xff, 0xff, 0xff, 0xff, 0xff, 0xff, 0xff, 0xff, 0xff, 0xff, 0xff, 0xff, 0xff, 0xff, 
  0xff, 0xff, 0xff, 0xff, 0xff, 0xff, 0xff, 0xff, 0xff, 0xff, 0xff, 0xff, 0xff, 0xff, 0xff, 0xff, 
  0xff, 0xff, 0xff, 0xff, 0xff, 0xff, 0xff, 0xff, 0xff, 0xff, 0xff, 0xff, 0xff, 0xff, 0xff, 0xff, 
  0xff, 0xff, 0xff, 0xff, 0xff, 0xff, 0xff, 0xff, 0xff, 0xff, 0xff, 0xff, 0xff, 0xff, 0xff, 0xff, 
  0xff, 0xff, 0xff, 0xff, 0xff, 0xff, 0xff, 0xff, 0xff, 0xff, 0xff, 0xff, 0xff, 0xff, 0xff, 0xff, 
  0xff, 0xff, 0xff, 0xff, 0xff, 0xff, 0xff, 0xff, 0xff, 0xff, 0xff, 0xff, 0xff, 0xff, 0xff, 0xff, 
  0xff, 0xff, 0xff, 0xff, 0xff, 0xff, 0xff, 0xff, 0xff, 0xff, 0xff, 0xff, 0xff, 0xff, 0xff, 0xff, 
  0xff, 0xff, 0xff, 0xff, 0xff, 0xff, 0xff, 0xff, 0xff, 0xff, 0xff, 0xff, 0xff, 0xff, 0xff, 0xff, 
  0xff, 0xff, 0xff, 0xff, 0xff, 0xff, 0xff, 0xff, 0xff, 0xff, 0xff, 0xff, 0xff, 0xff, 0xff, 0xff, 
  0xff, 0xff, 0xff, 0xff, 0xff, 0xff, 0xff, 0xff, 0xff, 0xff, 0xff, 0xff, 0xff, 0xff, 0xff, 0xff, 
  0xff, 0xff, 0xff, 0xff, 0xff, 0xff, 0xff, 0xff, 0xff, 0xff, 0xff, 0xff, 0xff, 0xff, 0xff, 0xff, 
  0xff, 0xff, 0xff, 0xff, 0xff, 0xff, 0xff, 0xff, 0xff, 0xff, 0xff, 0xff, 0xff, 0xff, 0xff, 0xff, 
  0xff, 0xff, 0xff, 0xff, 0xff, 0xff, 0xff, 0xff, 0xff, 0xff, 0xff, 0xff, 0xff, 0xff, 0xff, 0xff, 
  0xff, 0xff, 0xff, 0xff, 0xff, 0xff, 0xff, 0xff, 0xff, 0xff, 0xff, 0xff, 0xff, 0xff, 0xff, 0xff, 
  0xff, 0xff, 0xff, 0xff, 0xff, 0xff, 0xff, 0xff, 0xff, 0xff, 0xff, 0xff, 0xff, 0xff, 0xff, 0xff, 
  0xff, 0xff, 0xff, 0xff, 0xff, 0xff, 0xff, 0xff, 0xff, 0xff, 0xff, 0xff, 0xff, 0xff, 0xff, 0xff, 
  0xff, 0xff, 0xff, 0xff, 0xff, 0xff, 0xff, 0xff, 0xff, 0xff, 0xff, 0xff, 0xff, 0xff, 0xff, 0xff, 
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

};

void setup()
{
  // Start serial communication
  Serial.begin(256000);

  pinMode(buttonPin, INPUT_PULLUP);
  pinMode(buttonPin_2, INPUT_PULLUP);
  
  //Start load cell ADC communication
  scale.begin(LOADCELL_DOUT_PIN, LOADCELL_SCK_PIN);

  //Start LCD
  tft.begin();
  tft.setRotation(1);
  tft.fillScreen(BLACK);
  tft.setCursor(10, 10);
  tft.setTextColor(WHITE);  
  tft.setTextSize(1);

  // See if the card is present and can be initialized:
  if (!SD.begin(chipSelect)) 
  {
    Serial.println("Card failed, or not present");
    tft.println("Card failed, or not present");
    // don't do anything more:
    return;
  }
  tft.setCursor(110, 120);
  tft.println("Card initialized");
  Serial.println("card initialized");
  delay(1000);
  tft.fillScreen(BLACK);
  delay(1000);

  // Draw the bitmap:
  // drawBitmap(x position, y position, bitmap data, bitmap width, bitmap height, color)
  tft.drawBitmap(0, 0, logo, 320, 240, WHITE);
  delay(2000);
  tft.fillScreen(BLACK);
  
//  Serial.println("CLEARDATA");
//  Serial.println("LABEL,Realtime,Encoder,Load cell,Time(ms)");

  // Open the txt. file and add labels on each column
  //File dataFile = SD.open("data.txt", FILE_WRITE);
  //File dataFile = SD.open(fileName, FILE_WRITE);
  File dataFile = SD.open("data5.txt", FILE_WRITE);
   
  if (dataFile) 
    {
      dataFile.print("Subject Number");
      dataFile.print(";");
      dataFile.print("Encoder velocity (mm/s)");
      dataFile.print(";");
      dataFile.print("Load cell force (N)");
      dataFile.print(";");
      dataFile.println("Time (ms)");
      dataFile.close();
    }  
    // if the file isn't open, pop up an error:
    else 
    {
      Serial.println("error opening datalog.txt");
    } 
  
}

void loop()
{     
   
  for (x = 0; x <= 300; x += 1) 
  {
    //Push button reading
    read_push_button();

    //Read second Push button
    read_second_push_button();


    //Load cell reading
    //load_cell_reading = abs(scale.read()/500);
    load_cell_reading = scale.read();
    F = 0.0011*load_cell_reading - 1.248; //Force conversion using the load cell calibration equation
    
    // Rotational encoder reading
    if (rotatiional_flag == true)
      {
        //s = encoder.read()*dpr/ppr;
        s = encoder.read();
      }
      
    //Linear Encoder reading
    if (linear_flag == true)
      {
        s = -1*encoder.read();
      }

    //Save the data on the SD card
    save_sd_card();

    //Calculate the velocity at a certain interval
    if (Interval > milliseconds) 
      {
        if (rotatiional_flag == true)
        {
          v = ((s-s_i)*dpr/ppr)/(float(milliseconds)/1000); // deg per second
        }
        if (linear_flag == true)
        {
          //v = (((s-s_i)*mmpp)/1000)/(float(milliseconds)/1000); // meters per second
          v = ((s-s_i)*mmpp)/(float(milliseconds)/1000); // mm per second
        }

        s_i = s;
        Interval = 0;

        //Plot the selected sensor on the display
        if (state == 0)
          {
            Graph(tft, x, v, 30, 240, 320, 240, 0, 320, 100, 0, v_max, 100, "", "", "", WHITE, WHITE, BLUE, WHITE, BLACK, display1);
          }
                
        if (state == 1)
          {
            Graph(tft, x, F, 30, 240, 320, 240, 0, 320, 100, 0, F_max, 100, "", "", "", WHITE, WHITE, RED, WHITE, BLACK, display1);
          }
      }
  }
  tft.fillScreen(BLACK);
  display1 = true;
}

void save_sd_card()
{
  File dataFile = SD.open("Bosco.txt", FILE_WRITE);

  //sprintf(fileName, "%d.txt", count);
  //File dataFile = SD.open(fileName, FILE_WRITE);
  
  // if the file is available, write to it:
  if (dataFile) 
   {
     //dataFile.println(dataString);
     dataFile.print(count);
     dataFile.print(";");
     //dataFile.print(s);//Raw data
     dataFile.print(v);
     dataFile.print(";");
     //dataFile.print(load_cell_reading);//Raw data
     dataFile.print(F);//Force
     dataFile.print(";");
     dataFile.println(millis());
     dataFile.close();
   }  
   // if the file isn't open, pop up an error:
   else 
   {
     Serial.println("error opening datalog.txt");
   } 
  
}


void read_push_button()
{
  if (pushbutton.update()) 
  {
    if (pushbutton.fallingEdge()) 
    {
      state = !state;
      //count = count + 1;
    }
  } 
}

void read_second_push_button()
{
  if (pushbutton_2.update()) 
  {
    if (pushbutton_2.fallingEdge()) 
    {
      //state = !state;
      count = count + 1;
    }
  } 
}

void serial_print()
{
    Serial.print("DATA,TIME,");
    Serial.print(v);
    Serial.print(","); 
    Serial.print(load_cell_reading);
    Serial.print(","); 
    Serial.print(millis());
}
/*
  function to draw a cartesian coordinate system and plot whatever data you want
  just pass x and y and the graph will be drawn
  huge arguement list
  &d name of your display object
  x = x data point
  y = y datapont
  gx = x graph location (lower left)
  gy = y graph location (lower left)
  w = width of graph
  h = height of graph
  xlo = lower bound of x axis
  xhi = upper bound of x asis
  xinc = division of x axis (distance not count)
  ylo = lower bound of y axis
  yhi = upper bound of y asis
  yinc = division of y axis (distance not count)
  title = title of graph
  xlabel = x axis label
  ylabel = y axis label
  gcolor = graph line colors
  acolor = axis line colors
  pcolor = color of your plotted data
  tcolor = text color
  bcolor = background color
  &redraw = flag to redraw graph on fist call only
*/
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

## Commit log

2021-06-15 BOM Magnets Update
    [BOM.xlsx]
2021-06-21 3rd commit
    [Back cover.ipt, Encoder base.stl, Encoder base.stp, Front cover.ipt]
2021-06-28 SA 1.0.1
    [0603-CAP.ipt, 0603-RES.ipt, 0805.ipt, 1210.ipt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]
2021-07-02 SP 1.0.1 PMMA case 1
    [9V Battery.ipt, Adafruit 2.8TFT.ipt, Assembly3.0004.iam, Assembly3.iam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]
2021-07-02 SA 1.0.1 Component names
    [Sport Analyzer 1.0.1.brd]
2021-07-03 Conical pulley data
    [Artur1.xlsx, Xavi 1.xlsx]
2021-07-04 Prism files 1
    [Artur1.xlsx, Xavi 1.xlsx, Xavi 2.xlsx]
2021-07-10 SA 1.0.1 (4)
    [9V Battery.0002.ipt, 9V Battery.ipt, Assembly3.0009.iam, Assembly3.iam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]
2021-07-14 Data update
    [Artur1.xlsx]
2021-07-16 Isometric data
    [Artur1.xlsx, BOM.xlsx, Encoder calibration.xlsx, Isometric rot ext.xlsx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]
2021-07-19 Shoulder MVC data 2
    [3 reps each side Xavi Isometric rot ext.xlsx, Isometric rot ext.xlsx, Unilateral hip extension TRX 2 (1right,2left).xlsx]
2021-07-28 Calibration correction
    [Artur1.xlsx, Assembly3.0013.iam, Assembly3.iam, Conical.xlsx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]
2021-08-01 Documentation 1.0.1
    [3 reps each side Xavi Isometric rot ext.xlsx, Artur1.xlsx, Assembly3.0014.iam, Assembly3.iam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]
2021-08-05 Update Load cell calibration eq
    [Unilateral hip extension TRX 2 (1right,2left).xlsx]
2021-08-07 SD long recording fix
    [BOM.xlsx, Back cover.ipt, Back cover.stl, Bill of Materials.xlsx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]
2021-08-07 Inventor design files
    [0603-CAP.ipt, 0603-RES.ipt, 0805.ipt, 1210.ipt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]
2021-09-30 Bosco 60s test data 1
    [BOSCO.xlsx]
2021-10-01 pulses/mm correction
    [Encoder Calibration 1.xlsx]
2021-10-15 Assembly instructions
    [Assembly3.0002.ipn, Assembly3.0021.iam, Assembly3.iam, Assembly3.ipn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]
2021-10-15 Assembly instructions PDF
2021-10-15 Removed old folder
    [0603-CAP.ipt, 0603-RES.ipt, 0805.ipt, 1210.ipt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]
2021-10-21 Assembly instructions Figures 8-9
    [Load cell calibration.xlsx]
2021-11-18 Article writing 1
    [Load cell calibration.xlsx]
2021-11-25 Data update 2
    [3 reps each side Xavi Isometric rot ext.xlsx, Artur1.xlsx, BOSCO.xlsx, Conical.xlsx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]
2022-02-17 Update Bill of Materials.xlsx
    [Bill of Materials.xlsx]
2022-02-17 Conical data
    [Conical.xlsx]
2022-03-05 TFT soldering
2022-03-05 Battery holder
2022-03-10 Teensy 4 version
    [Sport Analyzer Teensy4.brd, Sport Analyzer Teensy4.sch]
2022-04-05 Teensy 4 logic level shifters V2
    [Sport Analyzer Teensy4 (Mosfets).brd, Sport Analyzer Teensy4 (Mosfets).sch]
2022-05-04 Teensy 4 update
    [Bottom PMMA Chronojump.ipt, Bottom PMMA Teensy4.0018.ipt, Bottom case Chronojump.dxf, Sport Analyzer Chronojump Teensy 4.brd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]
2022-05-18 Chronojump case
    [Bottom PMMA Chronojump.0021.ipt, Bottom PMMA Chronojump.ipt, Bottom PMMA Teensy 4.ipt, Bottom case Chronojump 1.dxf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]
2022-06-02 Teensy 4 CJ firmware
2022-06-08 Chronojump version RTC/4buttons
    [Sport Analyzer Chronojump Teensy 4 (4 buttons).brd, Sport Analyzer Chronojump Teensy 4 (4 buttons).sch]
2022-06-08 Create Sport Analyzer Chronojump Teensy 4 schematic.png
2022-06-10 RTC DS1302 v1
    [Sport Analyzer Chronojump Teensy 4 (4 buttons).brd, Sport Analyzer Chronojump Teensy 4 (4 buttons).sch]
2022-10-26 Load cell 160 Hz
    [Sport Analyzer Chronojump Teensy 4 (4 buttons) Load cell 160Hz.brd, Sport Analyzer Chronojump Teensy 4 (4 buttons) Load cell 160Hz.sch]

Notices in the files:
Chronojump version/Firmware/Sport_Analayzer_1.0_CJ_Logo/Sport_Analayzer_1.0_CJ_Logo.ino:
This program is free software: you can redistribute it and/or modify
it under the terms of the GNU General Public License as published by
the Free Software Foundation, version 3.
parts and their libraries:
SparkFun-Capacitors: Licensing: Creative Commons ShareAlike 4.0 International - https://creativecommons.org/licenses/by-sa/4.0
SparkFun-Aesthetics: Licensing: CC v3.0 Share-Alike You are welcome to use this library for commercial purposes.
